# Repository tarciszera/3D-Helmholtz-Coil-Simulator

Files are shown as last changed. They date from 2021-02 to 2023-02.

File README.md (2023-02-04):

Main refference: https://repositorio.ifsc.edu.br/bitstream/handle/123456789/2103/IFSC_TCC_Bobinas_de_Helmholtz.pdf?sequence=1&isAllowed=y

# 1. Helmholtz coil simulator

This project aim is to prototype some kind of system control it automaticaly and make some fields setups in static applications.

## Table of contents

  - [1. Helmholtz coil simulator](#1-helmholtz-coil-simulator)
  - [2. Base Knowledge](#2-base-knowledge)
  - [3. Helmholtz coils design](#3-helmholtz-coils-design)
    - [3.1. Simulator](#31-simulator)
        - [3.1.1. Input parameters:](#311-input-parameters)
        - [3.1.2. Console results](#312-console-results)
        - [3.1.3. Graphical Results](#313-graphical-results)
        - [3.1.4. Simulator results](#314-simulator-results)
      - [3.2. D models](#32-d-models)
        - [3.2.1. axis helmholtz coil 3D model](#321-axis-helmholtz-coil-3d-model)
      - [3.3. Coils winding](#33-coils-winding)
- [4. System applications](#4-system-applications)

# 2. Base Knowledge

To create a homogeneous field in some free space region, the concept used was the [Helmholtz coil] that can create a homogeneous field inward from the coils to the geometric center of the estructure, the more in the center, the more homogeneous the field is.

Exciting the coils with a known current generates a known [magnetic field] (H) that is related to the magnetic flux density (B) by the permeability ($\mu$) of the material, in this case the air ([1.00000037])

The B can [saturate] depending on the material, in this case it will not happen so there are no linearity problems

Knowing that the magnetic field will be linear, so a 3 axis Helmholtz coil can be design to generate the arbitrary homogeneous magnetic field, remembering that this system must compensate the [earth magnetic field]

# 3. Helmholtz coils design

## 3.1. Simulator

To design the needed helmholtz coils, an open source python library was used, [magpylib], this library is capable to calculate magnetic field, through analytical solutions, of permanent magnets and current lines or current loops.

In fact the application is static, so the helmholtz can projected as current loops placed in a helmholtz coil shape.

<p align="center">
  
</p>

 From the cross-cut section the parameters for the coils calculation can be extracted as the following figure:

<p align="center">
  
</p>

The details about the calculator can be seen in the [Helmholtz coil calculator] and [Auxiliar library] files. Giving some parameters to the calculator, it gives us the necessary coil diameter to achieve the desired field in the center of the coil and graphics that shows the field strenght in the 3 vectors of the field separeted (x,y,z) and from this an analysis can be made to determine the homogenity of the field generated by each coil, amplitude and angle error relative to the center in the desired homogeneous region. Following the input and the results in this project.

###  3.1.1. Input parameters:

Those are the input parameters for the calculator to find the diameter necessary the design each coil, following previous figure standards.

``` python
# have to use a little bit bigger value than wireExternalDiameter, if not, the wire will not fit inside
AllCoilsWireDiameter = (0.56 + 0.047)*1.09   # Wire diameter in mm (from dataSheet)

minRes = 0.06736                            # Ohms/m (from dataSheet)
nominal = 0.06940                           # Ohms/m (from dataSheet)
maxRes = 0.07153                            # Ohms/m (from dataSheet)

wireResistence = maxRes                     # Ohms/m (from dataSheet)

# z First Coil configuration

zInitialValueCoilDiameter = 80 # Initial value for the function that calculates the precise diameter

zCoilCurrent = 0.5             # Amperes
zLoopsInEachEvenLayer = 10     # The number of loops in each layer
zEvenLayers = 7                # The evenlayers always have to be equal to oddLayers or oddLayers + 1
zOddLayers = 7
zDesiredField = 1.25           # The desired field in the center of the Helmholtz coil

# y Second Coil configuration

yCoilCurrent = 0.5             # Amperes
yLoopsInEachEvenLayer = 6      # The number of loops in each layer
yEvenLayers = 3                # The evenlayers always have to be oddLayers + 1 or equal oddLayers
yOddLayers = 3
yDesiredField = 0.25           # The desired field in the center of the Helmholtz coil

# x Third Coil configuration

xCoilCurrent = 0.5             # Amperes
xLoopsInEachEvenLayer = 7      # The number of loops in each layer
xEvenLayers = 3                # The evenlayers always have to be oddLayers + 1 or equal oddLayers
xOddLayers = 3
xDesiredField = 0.25           # The desired field in the center of the Helmholtz coil
```
[main_script](./HelmholtzCoilCalculator.py)

[utils_lib](./magpylibUtils.py)

###  3.1.2. Console results

Those are the results that shows up in the standard output, in this case the console of spyder, those results can estimate how much wire in meters and the power in watts that will be dissipated on each helmholtz coil individualy.



###  3.1.3. Graphical Results

Those are the graphical results of the calculator. For each coil a graphic is generated with the amplitude of the magnetic field of a slice in the center of the coil, this slice must have the region of interest, it also displays a 3D graphic of what the system looks like. Those graphics can help to estimate the homogenity level of the whole region.

<p align="center">
  
  
</p>

<p align="center">
  
  
</p>

<p align="center">
  
  
</p>

As can be seen in the next figures, the calculator estimates the interference of the cables used to bring the current to the coils, the current passing throught them generates a field and it can be compared with the field generated for each coil. Just the field of the connectors is showed in the graphics. Another that can be seen is if the coils will be inside each other in the 3D representation, it's shown in the 3 coils figure that the coils don't touch each other in this case.

<p align="center">
  
  
</p>

<p align="center">
  
  
  
</p>

###  3.1.4. Simulator results

After checking all the homogenity and interference stuff, the interested parameters to construct the coils support are shown in the next table:

Wire External Diameter = 0.6 mm

|Coils| Radius | Coil Width| Coil Height|
|:-:|-|-|-|
| Inner | 42.5 mm | 6.6 mm | 9.65 mm |
| Middle | 56.15 mm | 4 mm | 5.5 mm |
| External | 66.5 mm | 4.65 mm | 5.5 mm |
**\* rouded values**

##  3.2. 3D model

With the high precision of the 3D printers ($\pm$ 1 $\mu$m) the idea was doing the 3 helmholtz coils all together in the same mechanical part, 1 piece. With this, the misalignment problems would desappear.

Misalignment example:
<p align="center">
  
</p>

To design the 3D model the utilized software was [solidWorks], a comercial software for 3D models design, good for geometric models. The design was made based in the simulating results. Besides the coils, the sensor and sample placement should be designed together with the coil, to make it easier to think the supports was separated and connected throught holes and pegs.

###  3.2.1. axis helmholtz coil 3D model

The 3 axis helmholtz coil 3D model design can be seen in the following images:

<p align="center">
  
  
  
</p>

It has some holes inside to attach the sensor support and a bigger hole in the middle for the cables to link the sensor to the system. In the bottom some support points to make the coil stable in the table.

##  3.3. Coils winding

After doing the windings really carefull, maintaining the [wire] stretched while doing each turn, it helped to get the wire really fit in the coils support. The arrangement to stretch the wire can be seen in the next image, its an improvised tool that makes some pressure in the reel, extremely important to make the coils the most near to the simulation position of the wires.

<p align="center">
  
  
</p>

 The [hot glue] was used to mantain the cables fixed in the coils suppor, the result of the 3 axis coil can be seen in the following image:

<p align="center">
  
  
</p>

Each of the six coils was done individualy, doing the inside coils first, and then connected with a solder point with the respective pair (2 coils in X direction to form the X helmholtz coil for example)

#  4. System applications

[Compass zero field demonstration]

[Compass zero field procedure]

[Compass zero field demonstration]:https://www.youtube.com/watch?v=eRR1c4607lU

[Compass zero field procedure]:https://www.youtube.com/watch?v=aR3ZOZWw4vM&t=

[Coil Features]:CoilFeatures.md

[magpylib]:https://github.com/magpylib/magpylib

[Helmholtz coil]:https://en.wikipedia.org/wiki/Helmholtz_coil

[magnetic field]:https://en.wikipedia.org/wiki/Magnetic_field

[earth magnetic field]:https://en.wikipedia.org/wiki/Earth%27s_magnetic_field

[1.00000037]:https://en.wikipedia.org/wiki/Permeability_(electromagnetism)

[saturate]:https://en.wikipedia.org/wiki/Saturation_(magnetic)

[coil img 1]:https://i.imgur.com/AkZzpYJ.jpg

[hot glue]:https://en.wikipedia.org/wiki/Hot-melt_adhesive

[Missing Image]:https://i.imgur.com/0EmAI26.png

[wire]:https://at.rs-online.com/web/p/kupferdrahte/0357750/

[Missing Image]:(https://i.imgur.com/0EmAI26.png)

[tiny Missing Image]:(https://i.imgur.com/zDgtWUj.png)

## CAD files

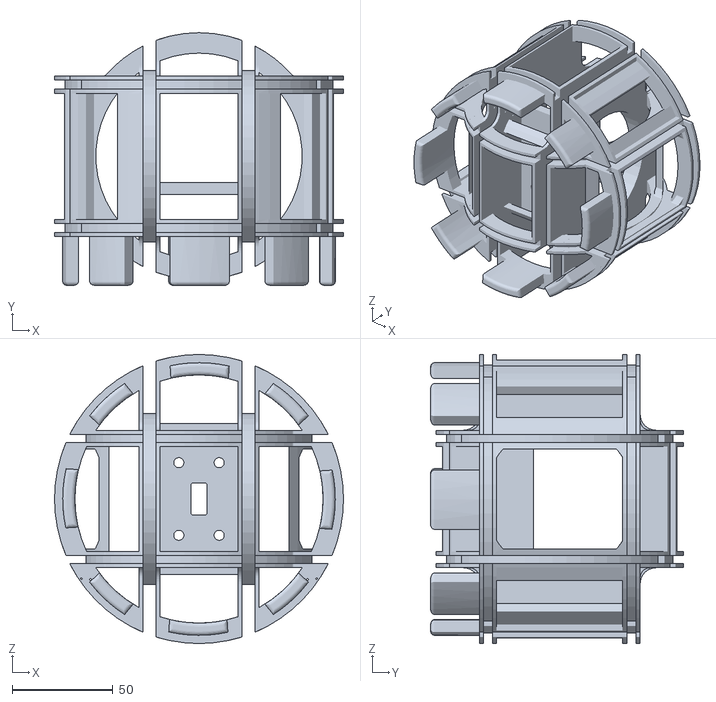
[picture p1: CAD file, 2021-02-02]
3DHC.STL
143.3 x 125.3 x 143.3
